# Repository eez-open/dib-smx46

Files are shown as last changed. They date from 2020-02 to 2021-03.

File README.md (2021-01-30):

OSHW-HR000004 (https://certification.oshwa.org/hr000004.html)

The EEZ DIB SMX46 module features programmable 4 x 6 switch matrix,  dual analog outputs and one power relay. 

### Feature list

* On-board STM32F030C6T6 or STM32F031C4T6 MCU
* 2 x 16-pin dual row 3.81 mm connectors
* 2 x ADIB connectors (10-pin 2 mm)
* 4 x 6 switch matrix (24 two-wire crosspoints), max. 2 A 
* 1 x power relay, max. 8 A / 230 Vac
* 2 x analog output 0 - 10 V, 10 mV set resolution (12-bit)
* On-board +3.3 V LDO
* Firmware download via UART
* Optional SWD for debugging
* I2C EEPROM for storing board specific parameters
* Dimensions: 146 x 95 mm, 2-layer PCB

### Firmware repository

https://github.com/eez-open/dib-smx46-fw

### r1B5 prototype

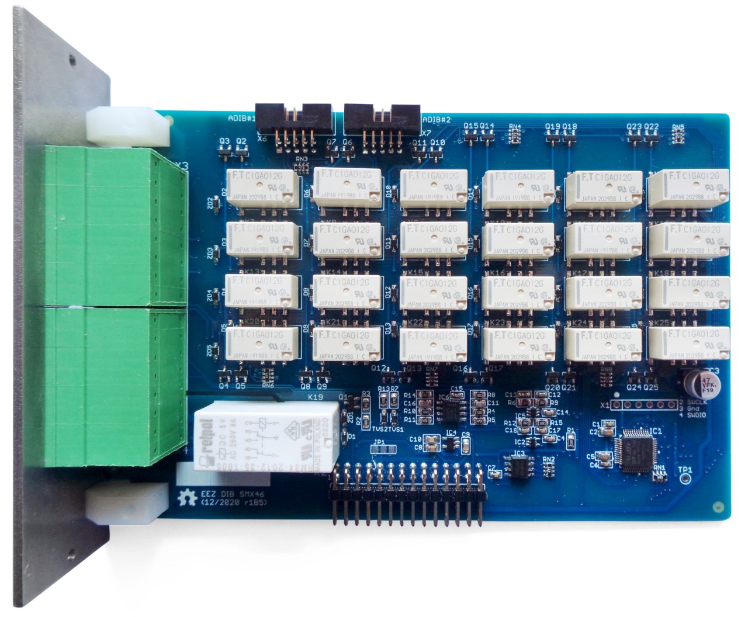
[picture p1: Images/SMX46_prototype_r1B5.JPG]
prototype


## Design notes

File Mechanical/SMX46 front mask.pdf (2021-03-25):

# SMX46

X1

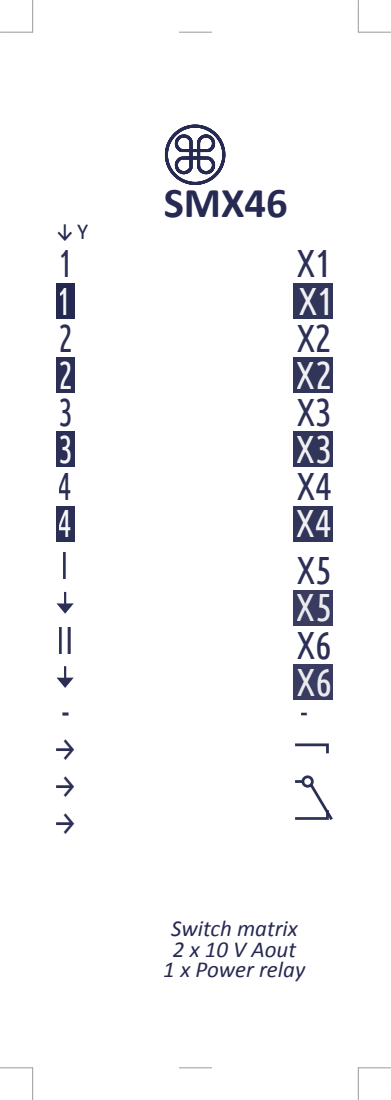
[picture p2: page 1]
Switch matrix 2 x 10 V Aout 1 x Power relay

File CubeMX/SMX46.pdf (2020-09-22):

## SMX46 Project Configuration Report

# 1. Description

## 1.1. Project

Project Name | SMX46
Board Name | custom
Generated with: | STM32CubeMX 5.6.1
Date | 09/22/2020

## 1.2. MCU

MCU Series | STM32F0
MCU Line | STM32F0x0 Value Line
MCU name | STM32F030C6Tx
MCU Package | LQFP48
MCU Pin number | 48

# 2. Pinout Configuration

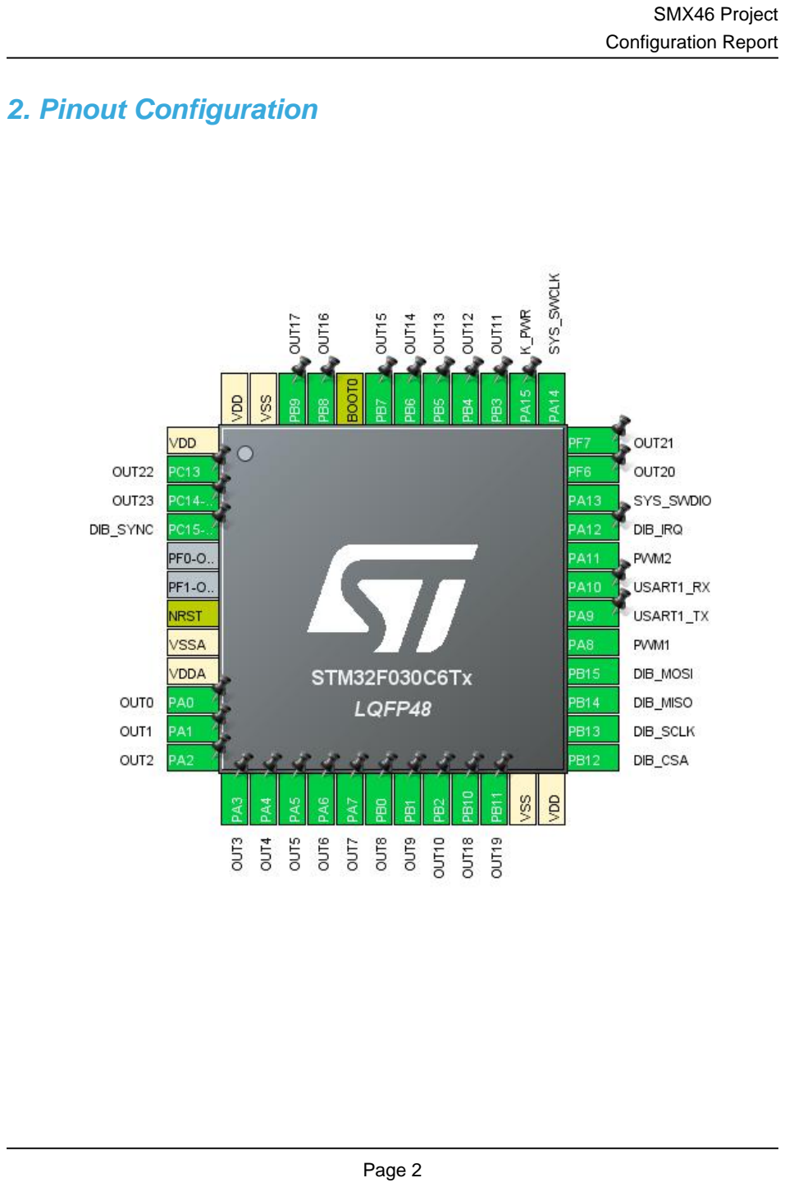
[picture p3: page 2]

# 3. Pins Configuration

Pin Number LQFP48 | Pin Name (function after reset) | Pin Type | Alternate Function(s) | Label
1 | VDD | Power
2 | PC13 * | I/O | GPIO_Output | OUT22
3 | PC14-OSC32_IN * | I/O | GPIO_Output | OUT23
4 | PC15-OSC32_OUT * | I/O | GPIO_Input | DIB_SYNC
7 | NRST | Reset
8 | VSSA | Power
9 | VDDA | Power
10 | PA0 * | I/O | GPIO_Output | OUT0
11 | PA1 * | I/O | GPIO_Output | OUT1
12 | PA2 * | I/O | GPIO_Output | OUT2
13 | PA3 * | I/O | GPIO_Output | OUT3
14 | PA4 * | I/O | GPIO_Output | OUT4
15 | PA5 * | I/O | GPIO_Output | OUT5
16 | PA6 * | I/O | GPIO_Output | OUT6
17 | PA7 * | I/O | GPIO_Output | OUT7
18 | PB0 * | I/O | GPIO_Output | OUT8
19 | PB1 * | I/O | GPIO_Output | OUT9
20 | PB2 * | I/O | GPIO_Output | OUT10
21 | PB10 * | I/O | GPIO_Output | OUT18
22 | PB11 * | I/O | GPIO_Output | OUT19
23 | VSS | Power
24 | VDD | Power
25 | PB12 | I/O | SPI1_NSS | DIB_CSA
26 | PB13 | I/O | SPI1_SCK | DIB_SCLK
27 | PB14 | I/O | SPI1_MISO | DIB_MISO
28 | PB15 | I/O | SPI1_MOSI | DIB_MOSI
29 | PA8 | I/O | TIM1_CH1 | PWM1
30 | PA9 | I/O | USART1_TX
31 | PA10 | I/O | USART1_RX
32 | PA11 | I/O | TIM1_CH4 | PWM2
33 | PA12 * | I/O | GPIO_Output | DIB_IRQ
34 | PA13 | I/O | SYS_SWDIO
35 | PF6 * | I/O | GPIO_Output | OUT20
36 | PF7 * | I/O | GPIO_Output | OUT21
37 | PA14 | I/O | SYS_SWCLK
38 | PA15 * | I/O | GPIO_Output | K_PWR

Pin Number LQFP48 | Pin Name (function after reset) | Pin Type | Alternate Function(s) | Label
39 | PB3 * | I/O | GPIO_Output | OUT11
40 | PB4 * | I/O | GPIO_Output | OUT12
41 | PB5 * | I/O | GPIO_Output | OUT13
42 | PB6 * | I/O | GPIO_Output | OUT14
43 | PB7 * | I/O | GPIO_Output | OUT15
44 | BOOT0 | Boot
45 | PB8 * | I/O | GPIO_Output | OUT16
46 | PB9 * | I/O | GPIO_Output | OUT17
47 | VSS | Power
48 | VDD | Power

## * The pin is affected with an I/O function

# 4. Clock Tree Configuration

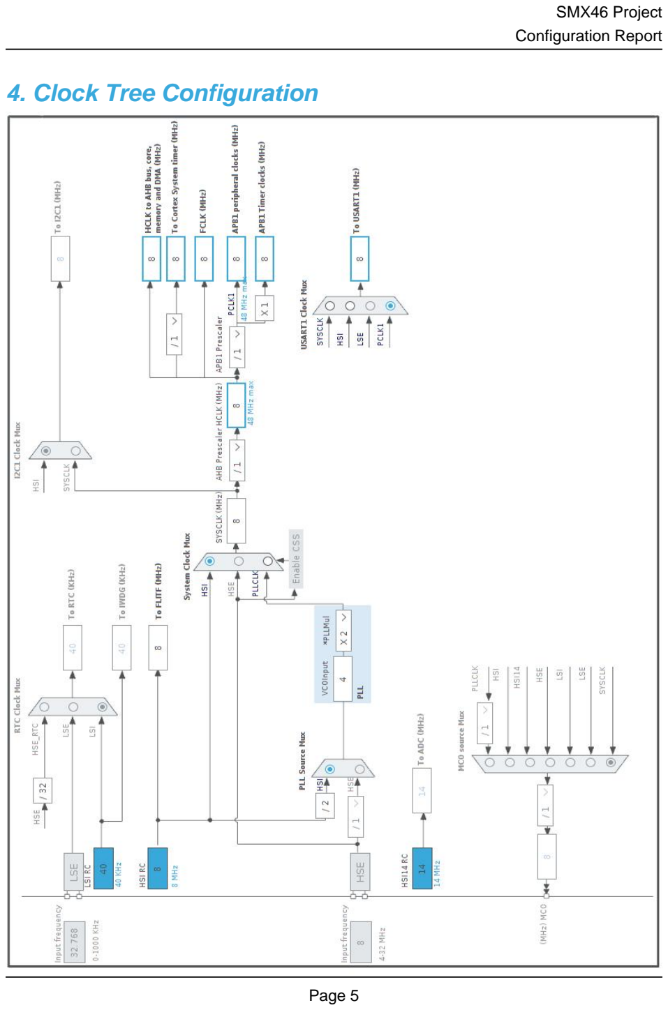
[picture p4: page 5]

# 5. Software Project

## 5.1. Project Settings

Name | Value
Project Name | SMX46
Project Folder | /home/denis/BACKUP/EEZ/Digital control/MCU/STM32/Projects/SMX46
Toolchain / IDE | EWARM V8.32
Firmware Package Name and Version | STM32Cube FW_F0 V1.11.0

## 5.2. Code Generation Settings

Name | Value
STM32Cube MCU packages and embedded software | Copy all used libraries into the project folder
Generate peripheral initialization as a pair of '.c/.h' files | No
Backup previously generated files when re-generating | No
Delete previously generated files when not re-generated | Yes
Set all free pins as analog (to optimize the power consumption) | No

# 6. Power Consumption Calculator report

### 6.1. Microcontroller Selection

Series | STM32F0
Line | STM32F0x0 Value Line
MCU | STM32F030C6Tx
Datasheet | 024849_Rev2

### 6.2. Parameter Selection

Temperature | 25
Vdd | 3.6

### 6.3. Battery Selection

Battery | Li-SOCL2(A3400)
Capacity | 3400.0 mAh
Self Discharge | 0.08 %/month
Nominal Voltage | 3.6 V
Max Cont Current | 100.0 mA
Max Pulse Current | 200.0 mA
Cells in series | 1
Cells in parallel | 1

## 6.4. Sequence

Step | Step1 | Step2
Mode | RUN | STOP
Vdd | 3.6 | 3.6
Voltage Source | Battery | Battery
Range | No Scale | No Scale
Fetch Type | FLASH | n/a
CPU Frequency | 48 MHz | 0 Hz
Clock Configuration | HSE PLL All IPs ON | Regulator_LP
Clock Source Frequency | 8 MHz | 0 Hz

### Peripherals

Additional Cons. | 0 mA | 0 mA
Average Current | 23.46 mA | 7.9 µA
Duration | 0.1 ms | 0.9 ms
DMIPS | 0.0 | 0.0
Ta Max | 100.36 | 105
Category | In DS Table | In DS Table

## 6.5. RESULTS

Sequence Time | 1 ms | Average Current | 2.35 mA
Battery Life | 1 month, 29 days, 16 hours | Average DMIPS | 0.0 DMIPS

## 6.6. Chart

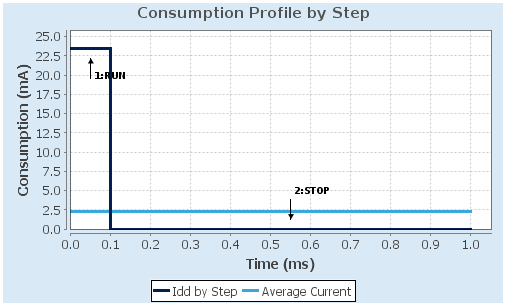
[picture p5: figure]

# 7. IPs and Middleware Configuration

# 7.1. CRC

## mode: Activated 7.1.1. Parameter Settings:

### Basic Parameters:

Default Polynomial State | Enable
Default Init Value State | Enable

### Advanced Parameters:

Input Data Inversion Mode | None
Output Data Inversion Mode | Disable
Input Data Format | Bytes

# 7.2. GPIO

# 7.3. SPI1

## Mode: Full-Duplex Slave Hardware NSS Signal: Hardware NSS Input Signal 7.3.1. Parameter Settings:

### Basic Parameters:

Frame Format | Motorola
Data Size | 4 Bits
First Bit | MSB First

### Clock Parameters:

Clock Polarity (CPOL) | Low
Clock Phase (CPHA) | 1 Edge

### Advanced Parameters:

CRC Calculation | Disabled
NSS Signal Type | Input Hardware

# 7.4. SYS

## mode: Debug Serial Wire Timebase Source: SysTick

# 7.5. TIM1

## Channel1: Output Compare CH1 Channel4: PWM Generation CH4 7.5.1. Parameter Settings:

### Counter Settings:

Prescaler (PSC - 16 bits value) | 0
Counter Mode | Up
Counter Period (AutoReload Register - 16 bits value ) | 0
Internal Clock Division (CKD) | No Division
Repetition Counter (RCR - 8 bits value) | 0
auto-reload preload | Disable

### Trigger Output (TRGO) Parameters:

Master/Slave Mode (MSM bit) | Disable (Trigger input effect not delayed)
Trigger Event Selection | Reset (UG bit from TIMx_EGR)

### Break And Dead Time management - BRK Configuration:

BRK State | Disable
BRK Polarity | High

### Break And Dead Time management - Output Configuration:

Automatic Output State | Disable
Off State Selection for Run Mode (OSSR) | Disable
Off State Selection for Idle Mode (OSSI) | Disable
Lock Configuration | Off

### Output Compare Channel 1:

Mode | Frozen (used for Timing base)
Pulse (16 bits value) | 0
Output compare preload | Disable
CH Polarity | High
CH Idle State | Reset

### PWM Generation Channel 4:

Mode | PWM mode 1
Pulse (16 bits value) | 0
Output compare preload | Enable
Fast Mode | Disable
CH Polarity | High
CH Idle State | Reset

# 7.6. USART1

## Mode: Asynchronous 7.6.1. Parameter Settings:

### Basic Parameters:

Baud Rate | 38400
Word Length | 8 Bits (including Parity)
Parity | None
Stop Bits | 1

### Advanced Parameters:

Data Direction | Receive and Transmit
Over Sampling | 16 Samples
Single Sample | Disable

### Advanced Features:

Auto Baudrate | Disable
TX Pin Active Level Inversion | Disable
RX Pin Active Level Inversion | Disable
Data Inversion | Disable
TX and RX Pins Swapping | Disable
Overrun | Enable
DMA on RX Error | Enable
MSB First | Disable

### * User modified value

# 8. System Configuration

# 8.1. GPIO configuration

IP | Pin | Signal | GPIO mode | GPIO pull/up pull down

## Max Speed

## User Label

SPI1 | PB12 | SPI1_NSS | Alternate Function Push Pull | No pull-up and no pull-down | High * | DIB_CSA
| PB13 | SPI1_SCK | Alternate Function Push Pull | No pull-up and no pull-down | High * | DIB_SCLK
| PB14 | SPI1_MISO | Alternate Function Push Pull | No pull-up and no pull-down | High * | DIB_MISO
| PB15 | SPI1_MOSI | Alternate Function Push Pull | No pull-up and no pull-down | High * | DIB_MOSI
SYS | PA13 | SYS_SWDIO | n/a | n/a | n/a
| PA14 | SYS_SWCLK | n/a | n/a | n/a
TIM1 | PA8 | TIM1_CH1 | Alternate Function Push Pull | No pull-up and no pull-down | Low | PWM1
| PA11 | TIM1_CH4 | Alternate Function Push Pull | No pull-up and no pull-down | Low | PWM2
USART1 | PA9 | USART1_TX | Alternate Function Push Pull | No pull-up and no pull-down | High *
| PA10 | USART1_RX | Alternate Function Push Pull | No pull-up and no pull-down | High *
GPIO | PC13 | GPIO_Output | Output Push Pull | No pull-up and no pull-down | Low | OUT22
| PC14- OSC32_IN | GPIO_Output | Output Push Pull | No pull-up and no pull-down | Low | OUT23
| PC15- OSC32_OU T | GPIO_Input | Input mode | No pull-up and no pull-down | n/a | DIB_SYNC
PA0 | GPIO_Output | Output Push Pull | No pull-up and no pull-down | Low | OUT0
PA1 | GPIO_Output | Output Push Pull | No pull-up and no pull-down | Low | OUT1
PA2 | GPIO_Output | Output Push Pull | No pull-up and no pull-down | Low | OUT2
PA3 | GPIO_Output | Output Push Pull | No pull-up and no pull-down | Low | OUT3
PA4 | GPIO_Output | Output Push Pull | No pull-up and no pull-down | Low | OUT4
PA5 | GPIO_Output | Output Push Pull | No pull-up and no pull-down | Low | OUT5
PA6 | GPIO_Output | Output Push Pull | No pull-up and no pull-down | Low | OUT6
PA7 | GPIO_Output | Output Push Pull | No pull-up and no pull-down | Low | OUT7
PB0 | GPIO_Output | Output Push Pull | No pull-up and no pull-down | Low | OUT8
PB1 | GPIO_Output | Output Push Pull | No pull-up and no pull-down | Low | OUT9
PB2 | GPIO_Output | Output Push Pull | No pull-up and no pull-down | Low | OUT10
PB10 | GPIO_Output | Output Push Pull | No pull-up and no pull-down | Low | OUT18
PB11 | GPIO_Output | Output Push Pull | No pull-up and no pull-down | Low | OUT19
PA12 | GPIO_Output | Output Push Pull | No pull-up and no pull-down | Low | DIB_IRQ
PF6 | GPIO_Output | Output Push Pull | No pull-up and no pull-down | Low | OUT20
PF7 | GPIO_Output | Output Push Pull | No pull-up and no pull-down | Low | OUT21
PA15 | GPIO_Output | Output Push Pull | No pull-up and no pull-down | Low | K_PWR
PB3 | GPIO_Output | Output Push Pull | No pull-up and no pull-down | Low | OUT11
PB4 | GPIO_Output | Output Push Pull | No pull-up and no pull-down | Low | OUT12

IP | Pin | Signal | GPIO mode | GPIO pull/up pull down | Max Speed | User Label
| PB5 | GPIO_Output | Output Push Pull | No pull-up and no pull-down | Low | OUT13
| PB6 | GPIO_Output | Output Push Pull | No pull-up and no pull-down | Low | OUT14
| PB7 | GPIO_Output | Output Push Pull | No pull-up and no pull-down | Low | OUT15
| PB8 | GPIO_Output | Output Push Pull | No pull-up and no pull-down | Low | OUT16
| PB9 | GPIO_Output | Output Push Pull | No pull-up and no pull-down | Low | OUT17

# 8.2. DMA configuration

DMA request | Stream | Direction | Priority
SPI1_RX | DMA1_Channel2 | Peripheral To Memory | Low
SPI1_TX | DMA1_Channel3 | Memory To Peripheral | Low

## SPI1_RX: DMA1_Channel2 DMA request Settings:

Mode: | Normal
Peripheral Increment: | Disable
Memory Increment: | Enable *
Peripheral Data Width: | Byte
Memory Data Width: | Byte

## SPI1_TX: DMA1_Channel3 DMA request Settings:

Mode: | Normal
Peripheral Increment: | Disable
Memory Increment: | Enable *
Peripheral Data Width: | Byte
Memory Data Width: | Byte

# 8.3. NVIC configuration

Interrupt Table | Enable | Preenmption Priority | SubPriority
Non maskable interrupt | true | 0 | 0
Hard fault interrupt | true | 0 | 0
System service call via SWI instruction | true | 0 | 0
Pendable request for system service | true | 0 | 0
System tick timer | true | 0 | 0
DMA1 channel 2 and 3 interrupts | true | 0 | 0
Flash global interrupt | unused
RCC global interrupt | unused
TIM1 break, update, trigger and commutation interrupts | unused
TIM1 capture compare interrupt | unused
SPI1 global interrupt | unused
USART1 global interrupt | unused

### * User modified value

# 9. Predefined Views - Category view : Current

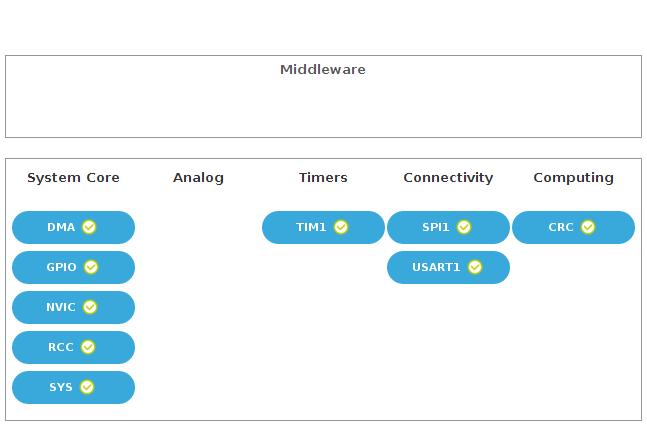
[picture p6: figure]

# 10. Software Pack Report

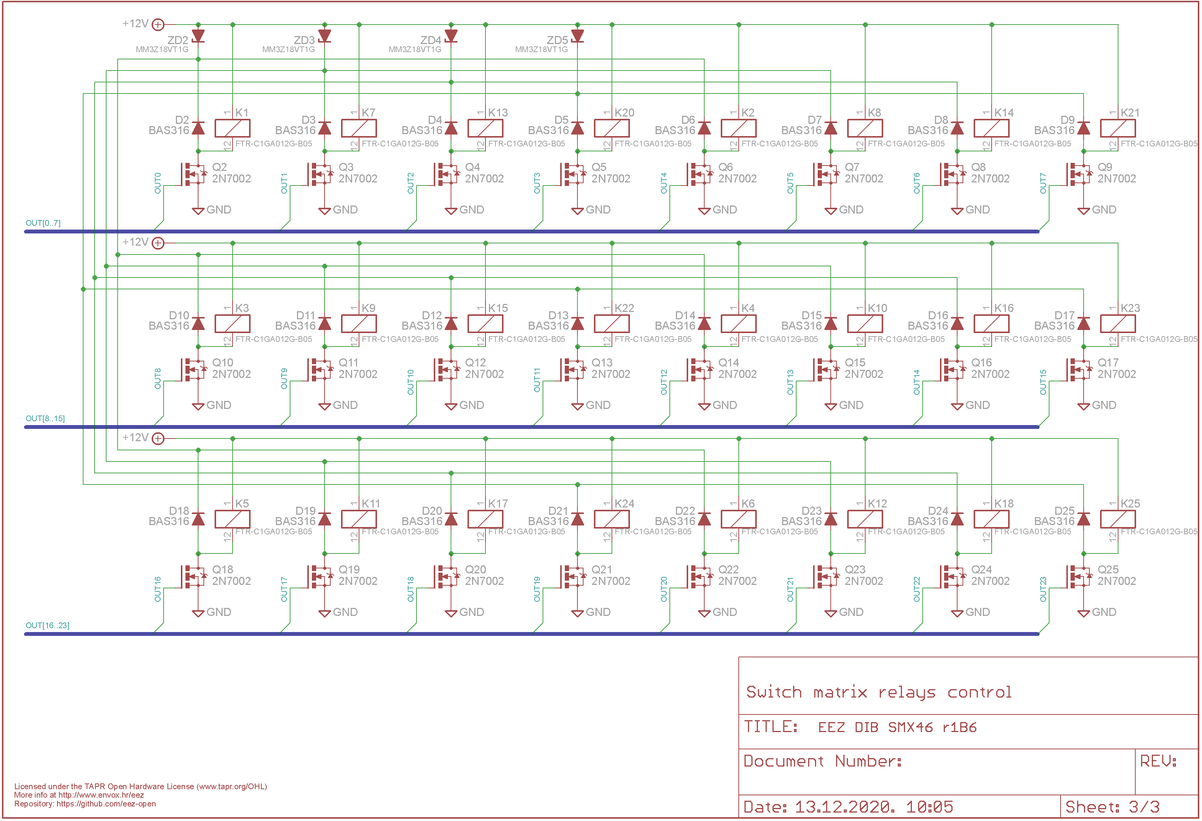
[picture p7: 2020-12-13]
EEZ DIB SMX46 r1B6 Sheet3of3.png

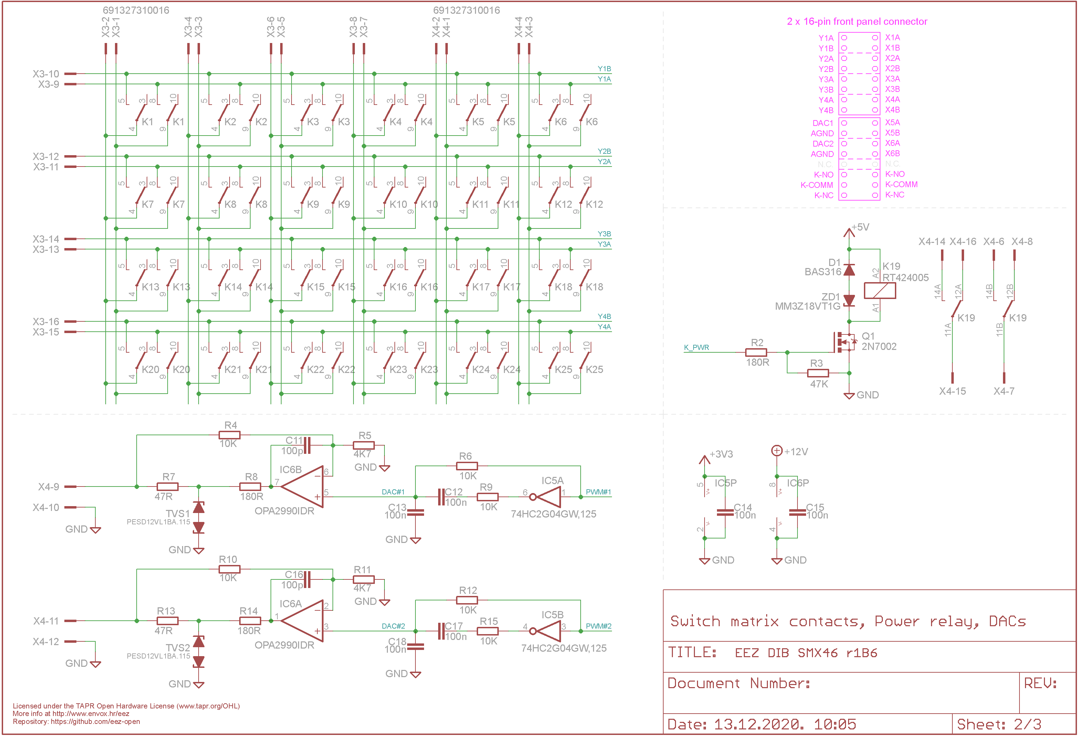
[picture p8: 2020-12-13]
EEZ DIB SMX46 r1B6 Sheet2of3.png

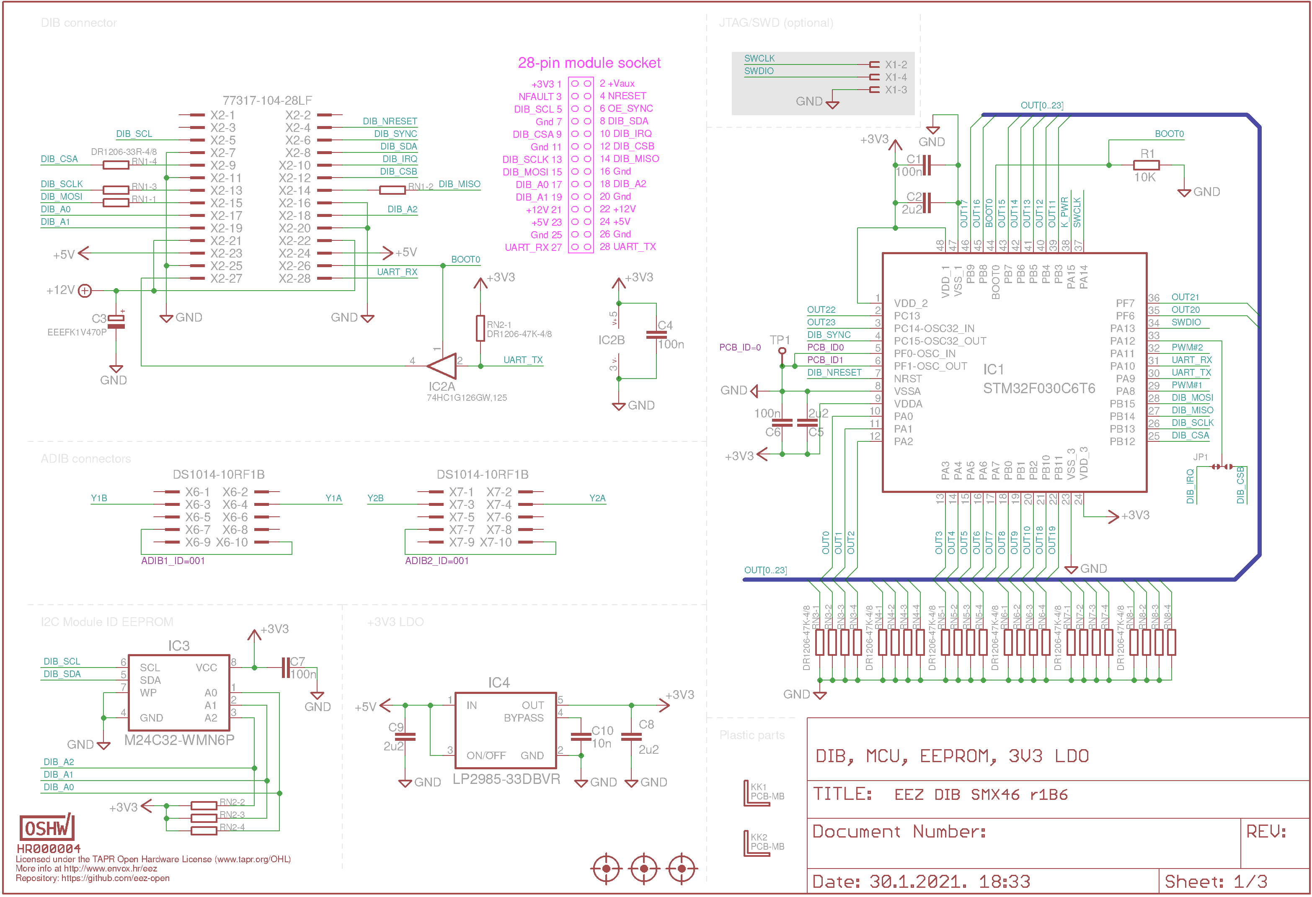
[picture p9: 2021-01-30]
EEZ DIB SMX46 r1B6 Sheet1of3.png

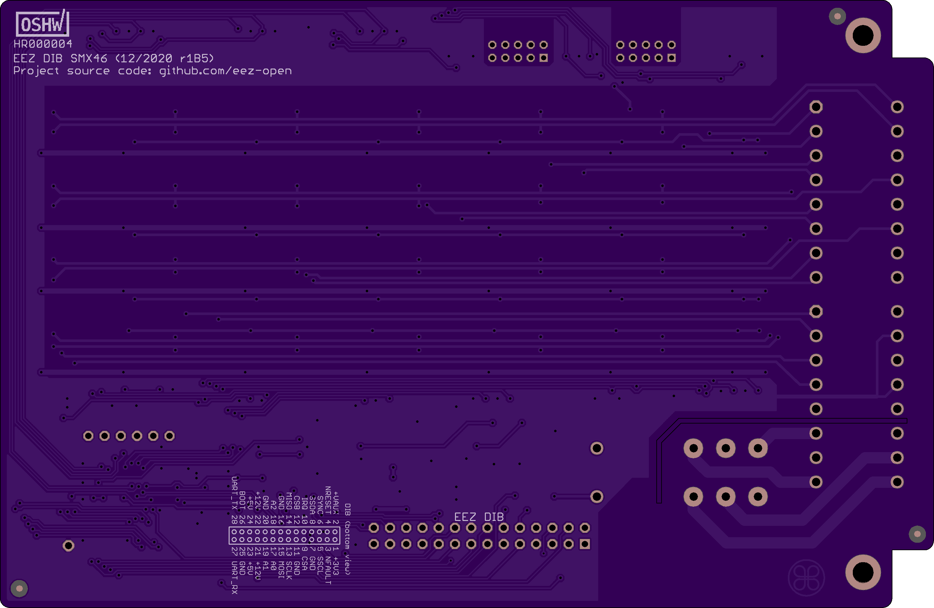
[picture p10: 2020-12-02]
Images/EEZ_DIB_SMX46_PCB_bottom.png

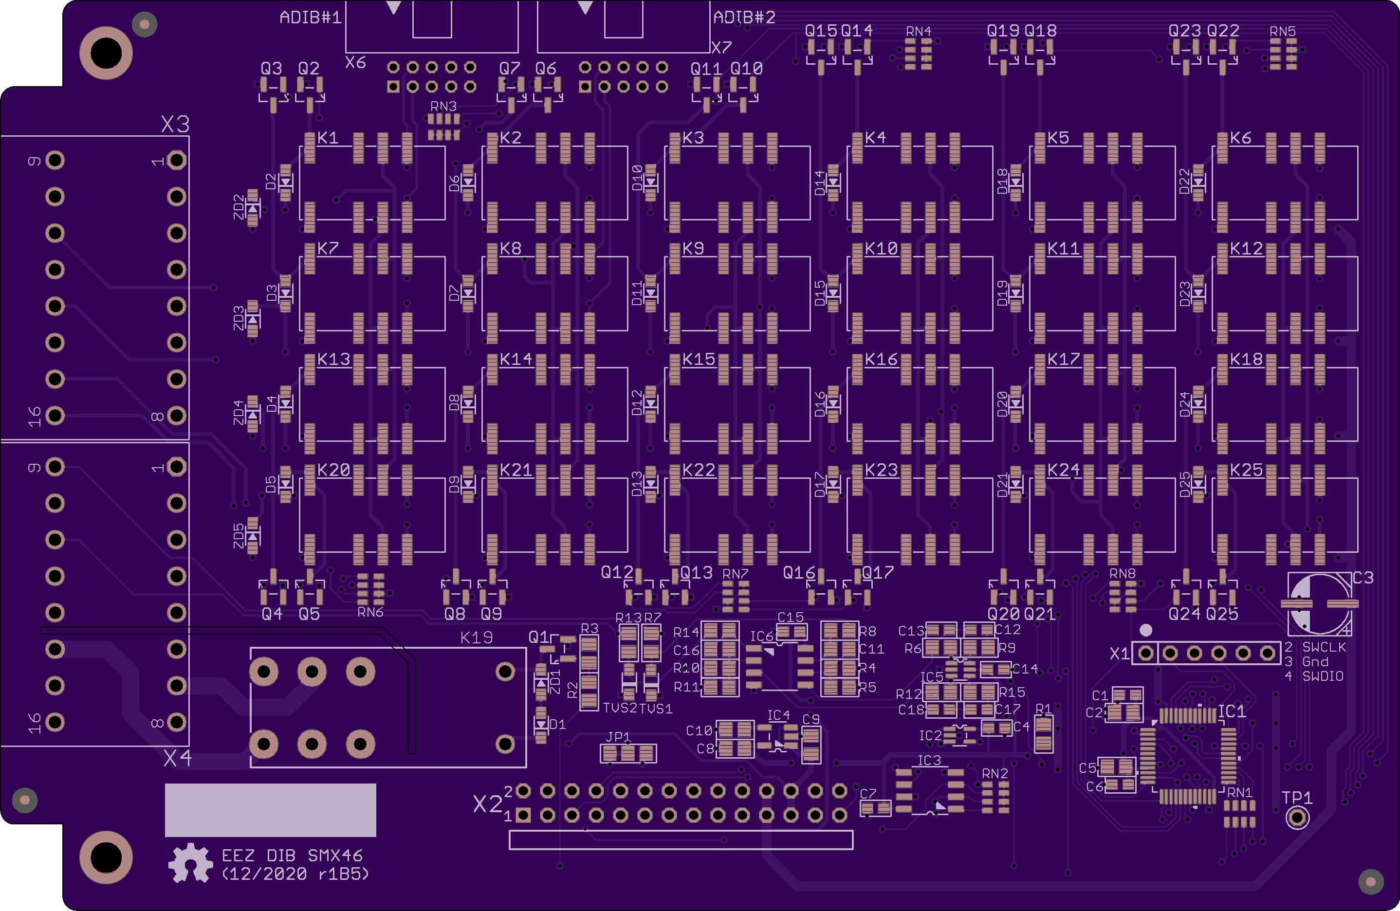
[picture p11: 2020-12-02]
Images/EEZ_DIB_SMX46_PCB_top.png

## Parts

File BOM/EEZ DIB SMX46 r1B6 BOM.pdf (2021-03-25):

EEZ DIB SMX46 BOM (r1B6, 2021-03-25) Project source code at https://github.com/eez-open/dib-prel6
Farnell / Element14 # Unit price Qty Part name Package Reference designator Code Part Number MOQ € | Digi-Key Unit price Part Number MOQ € | Mouser Unit price Part Number MOQ €
| | 80-C0603C104M4R
VJ0805Y103JXXP W1BC | | 710-885012207122
| | 80-C0805C101K5G
GRM21BR71C225 KA12L | | 80-C0805C225M4R ECLR
| | 667-EEE-FK1V470P

D1, D2, D3, D4, D5, D6, D7, D8, D9, D10, D11, D12, D13, D14, D15, D16, D17, D18, D19, D20, D21, D22, D23, D24, D25

| STM32F030C6T 6TR | 511-STM32F030C6T
Option: 2849912 STM32F031C4T6 2,510 1 STM32F031C4T6 | 497-13617-ND 2,200 | 6 STM32F031C4T 2,110 1 6
| | 771-HC1G126GW125
| | 511-M24C32-WMN6P
| | 595-LP2985-33DBVR
74HC2G04GW,125 74HC2G04GW,125 | | 771-HC2G04GW125
| | OPA2990IDR
K1, K2, K3, K4, K5, K6, K7, K8, K9, K10, K11, K12, K13, K14, K15, K16, K17, K18, K20, K21, K22, K23, K24, K2 | | 817-FTR-C1GA012GB05
1 | 10 100n | 0603 | 2522597 | 0,011 10 | 490-4774-1-ND | 0,029 100 | 0,007 100
2 | 1 10n | 0805 | C10 | 2896555 | 0,065 10 | 490-7194-1-ND | 0,017 | 10 | 0,036 10
3 | 2 100p | C0G, 0805 | C11, C16 | 2896861 | 0,023 10 | 399-15000-1-ND | 0,019 | 10 | 0,032 10
4 | 3 2u2 | 0805 | C2, C6, C8, C9 | 1828829 | 0,198 | 5 | 1276-2954-1-ND | 0,085 | 10 | 0,078 10
5 | 1 EEEFK1V470P | C3 | 9695850 | EEEFK1V470P | 0,344 | 1 | PCE3842CT-ND | 0,312 | 10 | 0,238 10
6 | 25 BAS316 | SOD-323 | 8734275 | BAS316,115 | 0,193 | 5 | 1727-7370-1-ND | 0,120 | 1 | 771-BAS316-T/R | 0,179 | 1
7 | 1 STM32F030C6T6 | LQFP-48 | IC1 | 2393632 | STM32F030C6T6 | 1,350 | 1 | 1,360 | 1 | 1,360 | 1
8 | 1 74HC1G126GW.125 | TSSOP-5 | IC2 | - | | | 1727-6037-1-ND | 0,360 | 1 | 0,369 | 1
9 | 1 M24C32-WMN6P | SOIC-8 | IC3 | 1224413 | M24C32-WMN6P | 0,212 | 5 | - | 0,210 | 1
10 | 1 | SOT-23-5 | IC4 | 1053660 | 0,610 | 1 | 296-18476-1-ND | 0,540 | 1 | 0,507 | 1
11 | 1 | IC5 | 2777732 | 0,283 | 5 | 1727-6045-1-ND | 0,274 | 10 | 0,248 10
12 | 1 | SOIC-8 | IC6 | - | | | 296-53506-1-ND | 1,210 | 1 | 1,360 | 1
13 | 24 FTR-C1GA012G-B05 | - | - | 3,320 10
14 | 1 RT424005 | K19 | 1629052 | RT424005 | 2,640 | 1 | PB1998-ND | 3,620 | 1 | 655-RT424005 | 2,820 | 1
15 | 25 2N7002 | SOT-23 | 1713825 | 2N7002K-7 | 0,148 | 5 | 0,126 | 10 | 0,113 10
16 | 7 10K | 0805 | 9237755 | 0,022 10 | 0,039 | 10 | 0,014 10
17 | 2 180R | 0805 | R2, R8, R14 | 2447583 | 0,007 10 | A126343CT-ND | 0,038 | 10 | 0,030 10
18 | 1 47K | 0805 | R3 | 2447664 | 0,009 10 | RHM47KKCT-ND | 0,036 | 10 | 0,014 10
19 | 2 4K7 | 0805 | R5, R11 | 2861530 | CRGCQ0805F4K7 | 0,012 10 | 0,040 | 10 | 0,027 10

C1, C4, C5, C7, C12, C13,
C14, C15, C17, C18

C0603C104K4RAC
7081

C0805C101JAGAC
TU
LP2985-33DBVR | LP2985A- 33DBVTE4 .
OPA2990IDR | 595-

THT; 8A relay
Q1, Q2, Q3, Q4, Q5, Q6, Q7, Q8, Q9, Q10, Q11, Q12, Q13, Q14, Q15, Q16, Q17, Q18, Q19, Q20, Q21, Q22, Q23, Q24, Q25 | T2N7002AKLMC T-ND | 757-T2N7002AKLM
| ND | 603-RC0805FR-0710KL
MCWR08X1800FT L | | 652-CR0805FX-1800ELF
| | 603-RC0805FR-0747KL
| 311-4.70KCRCT-ND | 603-RC0805FR-074K7L

R1, R4, R6, R9, R10, R12,
R15
RC0805FR-0710KL | 311-10.0KCRCT-

MCWR08X4702FT
L

# Qty Part name | RS Components | TME | Price calculation for 1 set

Unit price Code Part Number MOQ € | Unit price Code / Part Number MOQ € | THT SMD | | Line Cost €

1 10 100n

2 1 10n

3 2 100p

4 3 2u2

5 1 EEEFK1V470P

6 25 BAS316

7 1 STM32F030C6T6

8 1 74HC1G126GW.125

9 1 M24C32-WMN6P

10 1

11 1

12 1

13 24 FTR-C1GA012G-B05

14 1 RT424005
15 25 2N7002

16 7 10K

17 2 180R

18 1 47K

19 2 4K7

Option:
STM32F031C4T6

LP2985-33DBVR

74HC2G04GW,125

OPA2990IDR

393-6952 | 0,069 25 | CL10B104KA8NNNC | 0,098 100 | 10 | Mouser | 0,007 € 10 | 0,070
464-6672 | 0,026 50 | CC0805KRX7R9103 | 0,027 100 | 1 | Digikey | 0,017 € | 1 | 0,017
461-3997 | 0,030 50 | CL21C101JBANNNC | 0,026 100 | 2 | Digikey | 0,019 € | 2 | 0,038
766-1031 | 0,069 100 | CL21B225KOFNNNG | 0,071 100 | 3 | RS | 0,069 € | 3 | 0,207
537-0657 EEEFK1V470P | 0,394 | 5 | EEEFK1V470P | 0,130 | 5 | 1 | TME | 0,130 € | 1 | 0,130
397-2914 BAS316,115 | 0,122 50 | BAS316,115 | 0,026 25 | 25 | TME | 0,026 € 25 | 0,661
192-0993 | 0,972 | 5 | STM32F030C6T6 | 0,940 | 4 | 1 | TME | 0,940 € | 1 | 0,940
192-1080 | 2,152 | 5 | STM32F031C4T6 | 2,050 | 1
813-9282 | 0,024 100 | 74HC1G126GW.125 | 0,062 10 | 1 | RS | 0,024 € | 1 | 0,024
686-2453 | 0,180 25 | M24C32-WMN6P | 0,165 | 3 | 1 | TME | 0,165 € | 1 | 0,165
660-6733 LP2985-33DBVT | 0,737 | 1 | LP2985-33DBVR | 0,362 | 1 | 1 | TME | 0,362 € | 1 | 0,362
153-2919 | 0,235 50 | 74HC2G04GW.125 | 0,138 | 5 | 1 | TME | 0,138 € | 1 | 0,138
- | | | - | | | 1 | Digikey | 1,210 € | 1 | 1,210
195-8097 FTR-C1GA012G | 3,200 20 | FTR-C1GA012G-B05 | 0,840 25 | 24 | TME | 0,840 € 24 | 20,160
- | RT424005 | 1,150 | 5 | 1 | TME | 1,150 € | 1 | 1,150
671-0312 2N7002 | 1,250 20 | 2N7002LT1G | 0,019 25 | 25 | TME | 0,019 € 25 | 0,480
125-1189 CRG0805F10K | 0,002 100 | RC0805FR-0710K | 0,022 100 | 7 | RS | 0,002 € | 7 | 0,014
223-0326 CRG0805F180R | 0,090 50 | CQ05S8F1800T5E | 0,026 100 | 2 | Farnell | 0,007 € | 2 | 0,014
679-1434 | 0,036 50 | RC0805FR-0747K | 0,022 100 | 1 | Farnell | 0,009 € | 1 | 0,009
223-0528 CRG0805F4K7 | 0,023 50 | 0805S8F4701T5E | 0,023 100 | 2 | Farnell | 0,012 € | 2 | 0,023

Best
Supplier

Lowest
unit price
€

Order
Qty

VJ0603Y104KXJ
AT
08055C103KAT
2A
CC0805JRNP09
BN101
CL21B225KAFN
NNF

STM32F030C6T
6TR
STM32F031C4T
6
74HC1G126GW,
125
M24C32-
WMN6P

74HC2G04GW,1
25

CRCW080547K
0FKEA

Farnell / Element14 # Qty Part name Package Reference designator Code Part Number MOQ € | Digi-Key Part Number Unit price MOQ € | Mouser Part Number Unit price MOQ Unit price €
| | 279-CRGCQ0805F47 R
| CAY16-330J4LFCT-ND | 652-CAY16-330J4LF
| | 652-CAY16-473J4LF
PESD12VL1BA,11 5 | | 771-PESD12VL1BA-T/R
| | 649-77317-104-28LF
THT, 16-pin 3.81mm terminal MCD 1,5/ 8-G1-block header, male pins 3,81 | 732-691327310016-ND
20 | 2 47R | 0805 | R7, R13 | 2861899 | CRGCQ0805J47R | 0,007 10 | P47.0CCT-ND | 0,069 | 10 | 0,028 10
21 | 1 DR1206-33R-4/8 | 1206 resistor array | RN1 | 1770128 | CAY16-330J4LF | 0,069 10 | 0,090 | 1 | 0,085 | 1
22 | 7 | 1206 resistor array | 2787793 | CAY16-4702F4LF | 0,178 10 | CAY16-473J4LF | 0,080 | 10 | 0,016 10
23 | 2 PESD12VL1BA,115 | SOD-323 | TVS1, TVS2 | 8737363 | 0,365 | 5 | 1727-3808-1-ND | 0,320 | 10 | 0,296 10
24 | 1 77317-104-28LF | X2 | - | S2111EC-14-ND | 1,030 | 1 | 1,540 | 1
25 | 2 691327310016 | X3, X4 | 1793077 | 5,770 | 1 | 7,810 | 1 | 651-1843130 | 9,270 | 1
26 | 2 DS1014-10RF1B | X6, X7 | - | 2BHR-10-HUA | 0,650 | 1 | -
27 | 5 MM3Z18VT1G | SOD-323 | ZD1, ZD2, ZD3, ZD4, ZD5 | 1431193 | MM3Z18VT1G | 0,109 10 | 0,103 | 10 | 0,108 10

Not installed
1 N.C. | X1

Related parts and accessories
2 PMB-1 | PCB bracket; polyamide | KK1, KK2 | - | - | -
4 TJ0831530000G | 2579776 | EBK-08-B | 2,400 | 1 | 609-3803-ND | 1,760 | 1 | 1,530 | 1

Custom made components
1 | -
| All prices are net prices (without VAT)

All resistors are 1% 0805 and all capacitors are X7R 0805 if not otherwise specified.

DR1206-47K-4/8 | RN2, RN3, RN4, RN5, RN6, RN7, RN8

THT, 28-pin 0.1" header right angled

THT, 10-pin 2mm IDC, right angle
MM3Z18VT1GO
SCT-ND

863-
MM3Z18VT1G

8-pin 3.81mm pluggable
terminal block

649-220004-
D081B01LF

PCB 2-layer 146 x 95
mm

Please note that BOM does not contain ordering number for parts on reels or that which includes re-reeling fee (e.g. Farnell). Take also into account that total cost is higher because min. quantity (MOQ) for many parts is larger then what is needed for single unit.

# Qty Part name | RS Components | TME | Price calculation for 1 set

Code Part Number MOQ € | Code / Part Number Unit price MOQ € | THT SMD | | Line Cost € Unit price

20 2 47R

21 1 DR1206-33R-4/8

22 7

23 2 PESD12VL1BA,115

24 1 77317-104-28LF

25 2 691327310016

26 2 DS1014-10RF1B

27 5 MM3Z18VT1G

Not installed
1 N.C.

Related parts and accessories 2 PMB-1
4 TJ0831530000G

Custom made components
1

DR1206-47K-4/8

PCB 2-layer 146 x 95
mm

Best
Supplier

Lowest
unit price
€

Order
Qty
223-0253 CRG0805F47R | 0,016 50 | SMD0805-47R-1% | 0,022 100 | 2 | Farnell | 0,007 € | 2 | 0,013
522-5670 CAY16-330J4LF | 0,004 50 | 4D03WGJ0330T | 0,009 100 | 1 | RS | 0,004 € | 1 | 0,004
522-5759 CAY16-473J4LF | 0,020 50 | 4D03WGJ0473T | 0,013 100 | 7 | TME | 0,013 € | 7 | 0,091
508-024 | 0,294 20 | PESD12VL1BA.115 | 0,126 | 5 | 2 | TME | 0,126 € | 2 | 0,252
- | - | 1 | Digikey | 1,030 € | 1 | 1,030
191-1724 691327310016 | 7,900 | 1 | - | 2 | Farnell | 5,770 € | 2 | 11,540
- | DS1014-10RF1B | 0,220 | 3 | 2 | TME | 0,220 € | 2 | 0,440
802-4574 MM3Z18VT1G | 0,038 200 | MM3Z18VT1G | 0,025 25 | 5 | TME | 0,025 € | 5 | 0,126
6 | 126 | 39,31 €
1 | Farnell | 0,000 € | 1 | 0,000
- | PMB-1 | 0,072 10 | TME | 0,072 € | 2 | 0,145
- | 1,430 | 1 | TME | 1,430 € | 4 | 5,720

5,86 €

JLCPCB | 6,244 € | 1 | 6,244
| | | 6,24 €
| | Total | 51,42 €

PESD12VL1BA,
115

15EDGK-3.81-08P-14-
00A(H)

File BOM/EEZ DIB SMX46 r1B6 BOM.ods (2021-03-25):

 |  |  |  |  | Farnell / Element14 |  |  |  | Digi-Key |  |  | Mouser |  |  | RS Components |  |  |  | TME |  |  |  |  | Price calculation for 1 set
# | Qty | Part name | Package | Reference designator | Code | Part Number | Unit price € | MOQ | Part Number | Unit price € | MOQ | Part Number | Unit price € | MOQ | Code | Part Number | Unit price € | MOQ | Code / Part Number | Unit price € | MOQ | THT | SMD | Best Supplier | Lowest unit price € | Order Qty | Line Cost €
1 | 10 | 100n | 0603 | C1, C4, C5, C7, C12, C13, C14, C15, C17, C18 | 2522597 | C0603C104K4RAC7081 | 0,011 | 10 | 490-4774-1-ND | 0,029 | 100 | 80-C0603C104M4R | 0,007 | 100 | 393-6952 | VJ0603Y104KXJAT | 0,069 | 25 | CL10B104KA8NNNC | 0,098 | 100 |  | 10 | Mouser | 0,007 € | 10 | 0,070
2 | 1 | 10n | 0805 | C10 | 2896555 | VJ0805Y103JXXPW1BC | 0,065 | 10 | 490-7194-1-ND | 0,017 | 10 | 710-885012207122 | 0,036 | 10 | 464-6672 | 08055C103KAT2A | 0,026 | 50 | CC0805KRX7R9103 | 0,027 | 100 |  | 1 | Digikey | 0,017 € | 1 | 0,017
3 | 2 | 100p | C0G, 0805 | C11, C16 | 2896861 | C0805C101JAGACTU | 0,023 | 10 | 399-15000-1-ND | 0,019 | 10 | 80-C0805C101K5G | 0,032 | 10 | 461-3997 | CC0805JRNP09BN101 | 0,030 | 50 | CL21C101JBANNNC | 0,026 | 100 |  | 2 | Digikey | 0,019 € | 2 | 0,038
4 | 3 | 2u2 | 0805 | C2, C6, C8, C9 | 1828829 | GRM21BR71C225KA12L | 0,198 | 5 | 1276-2954-1-ND | 0,085 | 10 | 80-C0805C225M4RECLR | 0,078 | 10 | 766-1031 | CL21B225KAFNNNF | 0,069 | 100 | CL21B225KOFNNNG | 0,071 | 100 |  | 3 | RS | 0,069 € | 3 | 0,207
5 | 1 | EEEFK1V470P |  | C3 | 9695850 | EEEFK1V470P | 0,344 | 1 | PCE3842CT-ND | 0,312 | 10 | 667-EEE-FK1V470P | 0,238 | 10 | 537-0657 | EEEFK1V470P | 0,394 | 5 | EEEFK1V470P | 0,130 | 5 |  | 1 | TME | 0,130 € | 1 | 0,130
6 | 25 | BAS316 | SOD-323 | D1, D2, D3, D4, D5, D6, D7, D8, D9, D10, D11, D12, D13, D14, D15, D16, D17, D18, D19, D20, D21, D22, D23, D24, D25 | 8734275 | BAS316,115 | 0,193 | 5 | 1727-7370-1-ND | 0,120 | 1 | 771-BAS316-T/R | 0,179 | 1 | 397-2914 | BAS316,115 | 0,122 | 50 | BAS316,115 | 0,026 | 25 |  | 25 | TME | 0,026 € | 25 | 0,661
7 | 1 | STM32F030C6T6 | LQFP-48 | IC1 | 2393632 | STM32F030C6T6 | 1,350 | 1 | STM32F030C6T6TR | 1,360 | 1 | 511-STM32F030C6T6 | 1,360 | 1 | 192-0993 | STM32F030C6T6TR | 0,972 | 5 | STM32F030C6T6 | 0,940 | 4 |  | 1 | TME | 0,940 € | 1 | 0,940
 |  | Option: STM32F031C4T6 |  |  | 2849912 | STM32F031C4T6 | 2,510 | 1 | 497-13617-ND | 2,200 |  | STM32F031C4T6 | 2,110 | 1 | 192-1080 | STM32F031C4T6 | 2,152 | 5 | STM32F031C4T6 | 2,050 | 1
8 | 1 | 74HC1G126GW.125 | TSSOP-5 | IC2 | - |  |  |  | 1727-6037-1-ND | 0,360 | 1 | 771-HC1G126GW125 | 0,369 | 1 | 813-9282 | 74HC1G126GW,125 | 0,024 | 100 | 74HC1G126GW.125 | 0,062 | 10 |  | 1 | RS | 0,024 € | 1 | 0,024
9 | 1 | M24C32-WMN6P | SOIC-8 | IC3 | 1224413 | M24C32-WMN6P | 0,212 | 5 | - |  |  | 511-M24C32-WMN6P | 0,210 | 1 | 686-2453 | M24C32-WMN6P | 0,180 | 25 | M24C32-WMN6P | 0,165 | 3 |  | 1 | TME | 0,165 € | 1 | 0,165
10 | 1 | LP2985-33DBVR | SOT-23-5 | IC4 | 1053660 | LP2985A-33DBVTE4 . | 0,610 | 1 | 296-18476-1-ND | 0,540 | 1 | 595-LP2985-33DBVR | 0,507 | 1 | 660-6733 | LP2985-33DBVT | 0,737 | 1 | LP2985-33DBVR | 0,362 | 1 |  | 1 | TME | 0,362 € | 1 | 0,362
11 | 1 | 74HC2G04GW,125 |  | IC5 | 2777732 | 74HC2G04GW,125 | 0,283 | 5 | 1727-6045-1-ND | 0,274 | 10 | 771-HC2G04GW125 | 0,248 | 10 | 153-2919 | 74HC2G04GW,125 | 0,235 | 50 | 74HC2G04GW.125 | 0,138 | 5 |  | 1 | TME | 0,138 € | 1 | 0,138
12 | 1 | OPA2990IDR | SOIC-8 | IC6 | - |  |  |  | 296-53506-1-ND | 1,210 | 1 | 595-OPA2990IDR | 1,360 | 1 | - |  |  |  | - |  |  |  | 1 | Digikey | 1,210 € | 1 | 1,210
13 | 24 | FTR-C1GA012G-B05 |  | K1, K2, K3, K4, K5, K6, K7, K8, K9, K10, K11, K12, K13, K14, K15, K16, K17, K18, K20, K21, K22, K23, K24, K2 | - |  |  |  | - |  |  | 817-FTR-C1GA012GB05 | 3,320 | 10 | 195-8097 | FTR-C1GA012G | 3,200 | 20 | FTR-C1GA012G-B05 | 0,840 | 25 |  | 24 | TME | 0,840 € | 24 | 20,160
14 | 1 | RT424005 | THT; 8A relay | K19 | 1629052 | RT424005 | 2,640 | 1 | PB1998-ND | 3,620 | 1 | 655-RT424005 | 2,820 | 1 | - |  |  |  | RT424005 | 1,150 | 5 | 1 |  | TME | 1,150 € | 1 | 1,150
15 | 25 | 2N7002 | SOT-23 | Q1, Q2, Q3, Q4, Q5, Q6, Q7, Q8, Q9, Q10, Q11, Q12, Q13, Q14, Q15, Q16, Q17, Q18, Q19, Q20, Q21, Q22, Q23, Q24, Q25 | 1713825 | 2N7002K-7 | 0,148 | 5 | T2N7002AKLMCT-ND | 0,126 | 10 | 757-T2N7002AKLM | 0,113 | 10 | 671-0312 | 2N7002 | 1,250 | 20 | 2N7002LT1G | 0,019 | 25 |  | 25 | TME | 0,019 € | 25 | 0,480
16 | 7 | 10K | 0805 | R1, R4, R6, R9, R10, R12, R15 | 9237755 | RC0805FR-0710KL | 0,022 | 10 | 311-10.0KCRCT-ND | 0,039 | 10 | 603-RC0805FR-0710KL | 0,014 | 10 | 125-1189 | CRG0805F10K | 0,002 | 100 | RC0805FR-0710K | 0,022 | 100 |  | 7 | RS | 0,002 € | 7 | 0,014
17 | 2 | 180R | 0805 | R2, R8, R14 | 2447583 | MCWR08X1800FTL | 0,007 | 10 | A126343CT-ND | 0,038 | 10 | 652-CR0805FX-1800ELF | 0,030 | 10 | 223-0326 | CRG0805F180R | 0,090 | 50 | CQ05S8F1800T5E | 0,026 | 100 |  | 2 | Farnell | 0,007 € | 2 | 0,014
18 | 1 | 47K | 0805 | R3 | 2447664 | MCWR08X4702FTL | 0,009 | 10 | RHM47KKCT-ND | 0,036 | 10 | 603-RC0805FR-0747KL | 0,014 | 10 | 679-1434 | CRCW080547K0FKEA | 0,036 | 50 | RC0805FR-0747K | 0,022 | 100 |  | 1 | Farnell | 0,009 € | 1 | 0,009
19 | 2 | 4K7 | 0805 | R5, R11 | 2861530 | CRGCQ0805F4K7 | 0,012 | 10 | 311-4.70KCRCT-ND | 0,040 | 10 | 603-RC0805FR-074K7L | 0,027 | 10 | 223-0528 | CRG0805F4K7 | 0,023 | 50 | 0805S8F4701T5E | 0,023 | 100 |  | 2 | Farnell | 0,012 € | 2 | 0,023
20 | 2 | 47R | 0805 | R7, R13 | 2861899 | CRGCQ0805J47R | 0,007 | 10 | P47.0CCT-ND | 0,069 | 10 | 279-CRGCQ0805F47R | 0,028 | 10 | 223-0253 | CRG0805F47R | 0,016 | 50 | SMD0805-47R-1% | 0,022 | 100 |  | 2 | Farnell | 0,007 € | 2 | 0,013
21 | 1 | DR1206-33R-4/8 | 1206 resistor array | RN1 | 1770128 | CAY16-330J4LF | 0,069 | 10 | CAY16-330J4LFCT-ND | 0,090 | 1 | 652-CAY16-330J4LF | 0,085 | 1 | 522-5670 | CAY16-330J4LF | 0,004 | 50 | 4D03WGJ0330T | 0,009 | 100 |  | 1 | RS | 0,004 € | 1 | 0,004
22 | 7 | DR1206-47K-4/8 | 1206 resistor array | RN2, RN3, RN4, RN5, RN6, RN7, RN8 | 2787793 | CAY16-4702F4LF | 0,178 | 10 | CAY16-473J4LF | 0,080 | 10 | 652-CAY16-473J4LF | 0,016 | 10 | 522-5759 | CAY16-473J4LF | 0,020 | 50 | 4D03WGJ0473T | 0,013 | 100 |  | 7 | TME | 0,013 € | 7 | 0,091
23 | 2 | PESD12VL1BA,115 | SOD-323 | TVS1, TVS2 | 8737363 | PESD12VL1BA,115 | 0,365 | 5 | 1727-3808-1-ND | 0,320 | 10 | 771-PESD12VL1BA-T/R | 0,296 | 10 | 508-024 | PESD12VL1BA,115 | 0,294 | 20 | PESD12VL1BA.115 | 0,126 | 5 |  | 2 | TME | 0,126 € | 2 | 0,252
24 | 1 | 77317-104-28LF | THT, 28-pin 0.1" header right angled | X2 | - |  |  |  | S2111EC-14-ND | 1,030 | 1 | 649-77317-104-28LF | 1,540 | 1 | - |  |  |  | - |  |  | 1 |  | Digikey | 1,030 € | 1 | 1,030
25 | 2 | 691327310016 | THT, 16-pin 3.81mm terminal block header, male pins | X3, X4 | 1793077 | MCD 1,5/ 8-G1-3,81 | 5,770 | 1 | 732-691327310016-ND | 7,810 | 1 | 651-1843130 | 9,270 | 1 | 191-1724 | 691327310016 | 7,900 | 1 | - |  |  | 2 |  | Farnell | 5,770 € | 2 | 11,540
26 | 2 | DS1014-10RF1B | THT, 10-pin 2mm IDC, right angle | X6, X7 | - |  |  |  | 2BHR-10-HUA | 0,650 | 1 | - |  |  | - |  |  |  | DS1014-10RF1B | 0,220 | 3 | 2 |  | TME | 0,220 € | 2 | 0,440
27 | 5 | MM3Z18VT1G | SOD-323 | ZD1, ZD2, ZD3, ZD4, ZD5 | 1431193 | MM3Z18VT1G | 0,109 | 10 | MM3Z18VT1GOSCT-ND | 0,103 | 10 | 863-MM3Z18VT1G | 0,108 | 10 | 802-4574 | MM3Z18VT1G | 0,038 | 200 | MM3Z18VT1G | 0,025 | 25 |  | 5 | TME | 0,025 € | 5 | 0,126
 |  |  |  |  |  |  |  |  |  |  |  |  |  |  |  |  |  |  |  |  |  | 6 | 126 |  |  |  | 39,31 €
 |  | Not installed
 | 1 | N.C. |  | X1 |  |  |  |  |  |  |  |  |  |  |  |  |  |  |  |  |  |  | 1 | Farnell | 0,000 € | 1 | 0,000
 |  | Related parts and accessories
 | 2 | PMB-1 | PCB bracket; polyamide | KK1, KK2 | - |  |  |  | - |  |  | - |  |  | - |  |  |  | PMB-1 | 0,072 | 10 |  |  | TME | 0,072 € | 2 | 0,145
 | 4 | TJ0831530000G | 8-pin 3.81mm pluggable terminal block |  | 2579776 | EBK-08-B | 2,400 | 1 | 609-3803-ND | 1,760 | 1 | 649-220004-D081B01LF | 1,530 | 1 | - |  |  |  | 15EDGK-3.81-08P-14-00A(H) | 1,430 | 1 |  |  | TME | 1,430 € | 4 | 5,720
 |  |  |  |  |  |  |  |  |  |  |  |  |  |  |  |  |  |  |  |  |  |  |  |  |  |  | 5,86 €
 |  | Custom made components
 | 1 | PCB 2-layer 146 x 95 mm |  | - |  |  |  |  |  |  |  |  |  |  |  |  |  |  |  |  |  |  |  | JLCPCB | 6,244 € | 1 | 6,244
 |  |  |  |  |  |  |  |  |  |  |  |  |  |  |  |  |  |  |  |  |  |  |  |  |  |  | 6,24 €
 |  |  | All prices are net prices (without VAT)
 |  |  |  |  |  |  |  |  |  |  |  |  |  |  |  |  |  |  |  |  |  |  |  |  |  | Total | 51,42 €
 |  |  | Please note that BOM does not contain ordering number for parts on reels or that which includes re-reeling fee (e.g. Farnell). Take also into account that total cost is higher because min. quantity (MOQ) for many parts is larger then what is needed for single unit.
 |  |  | All resistors are 1% 0805 and all capacitors are X7R 0805 if not otherwise specified.

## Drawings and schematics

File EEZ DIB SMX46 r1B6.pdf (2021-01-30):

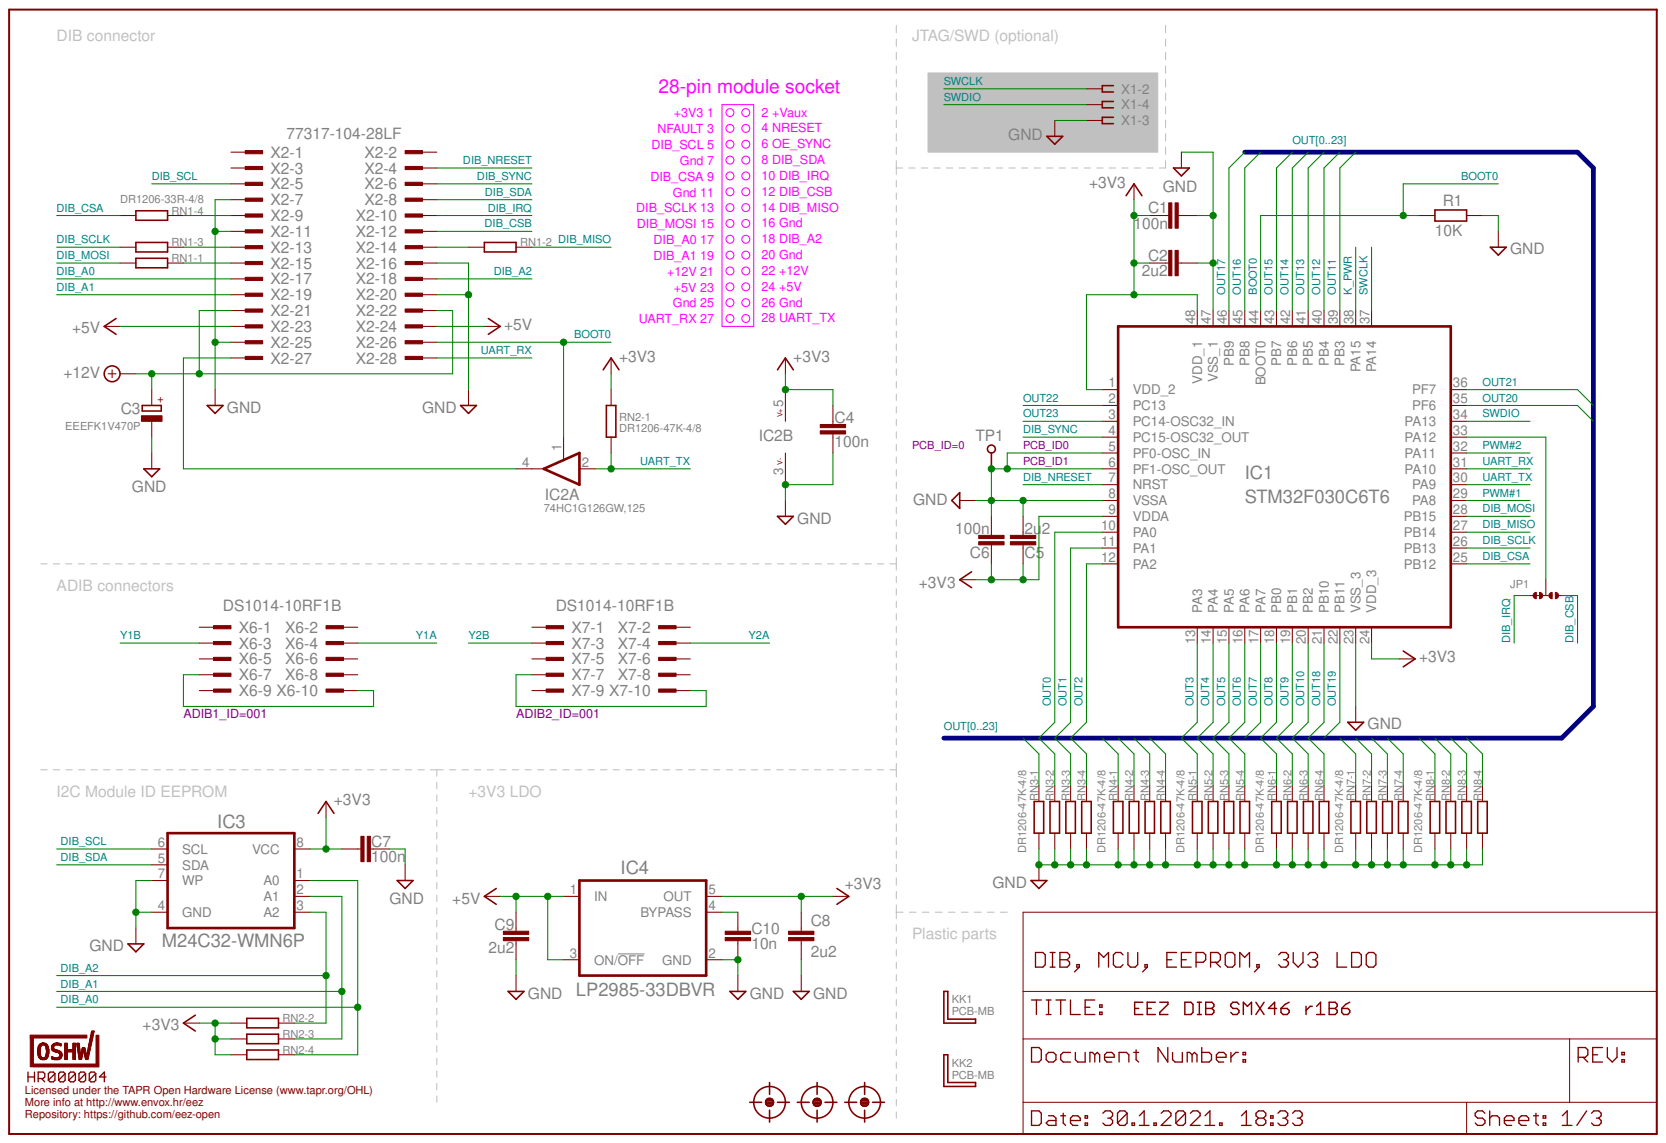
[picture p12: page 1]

Licensed under the TAPR Open Hardware License (www.tapr.org/OHL) Repository: https://github.com/eez-open More info at http://www.envox.hr/eez

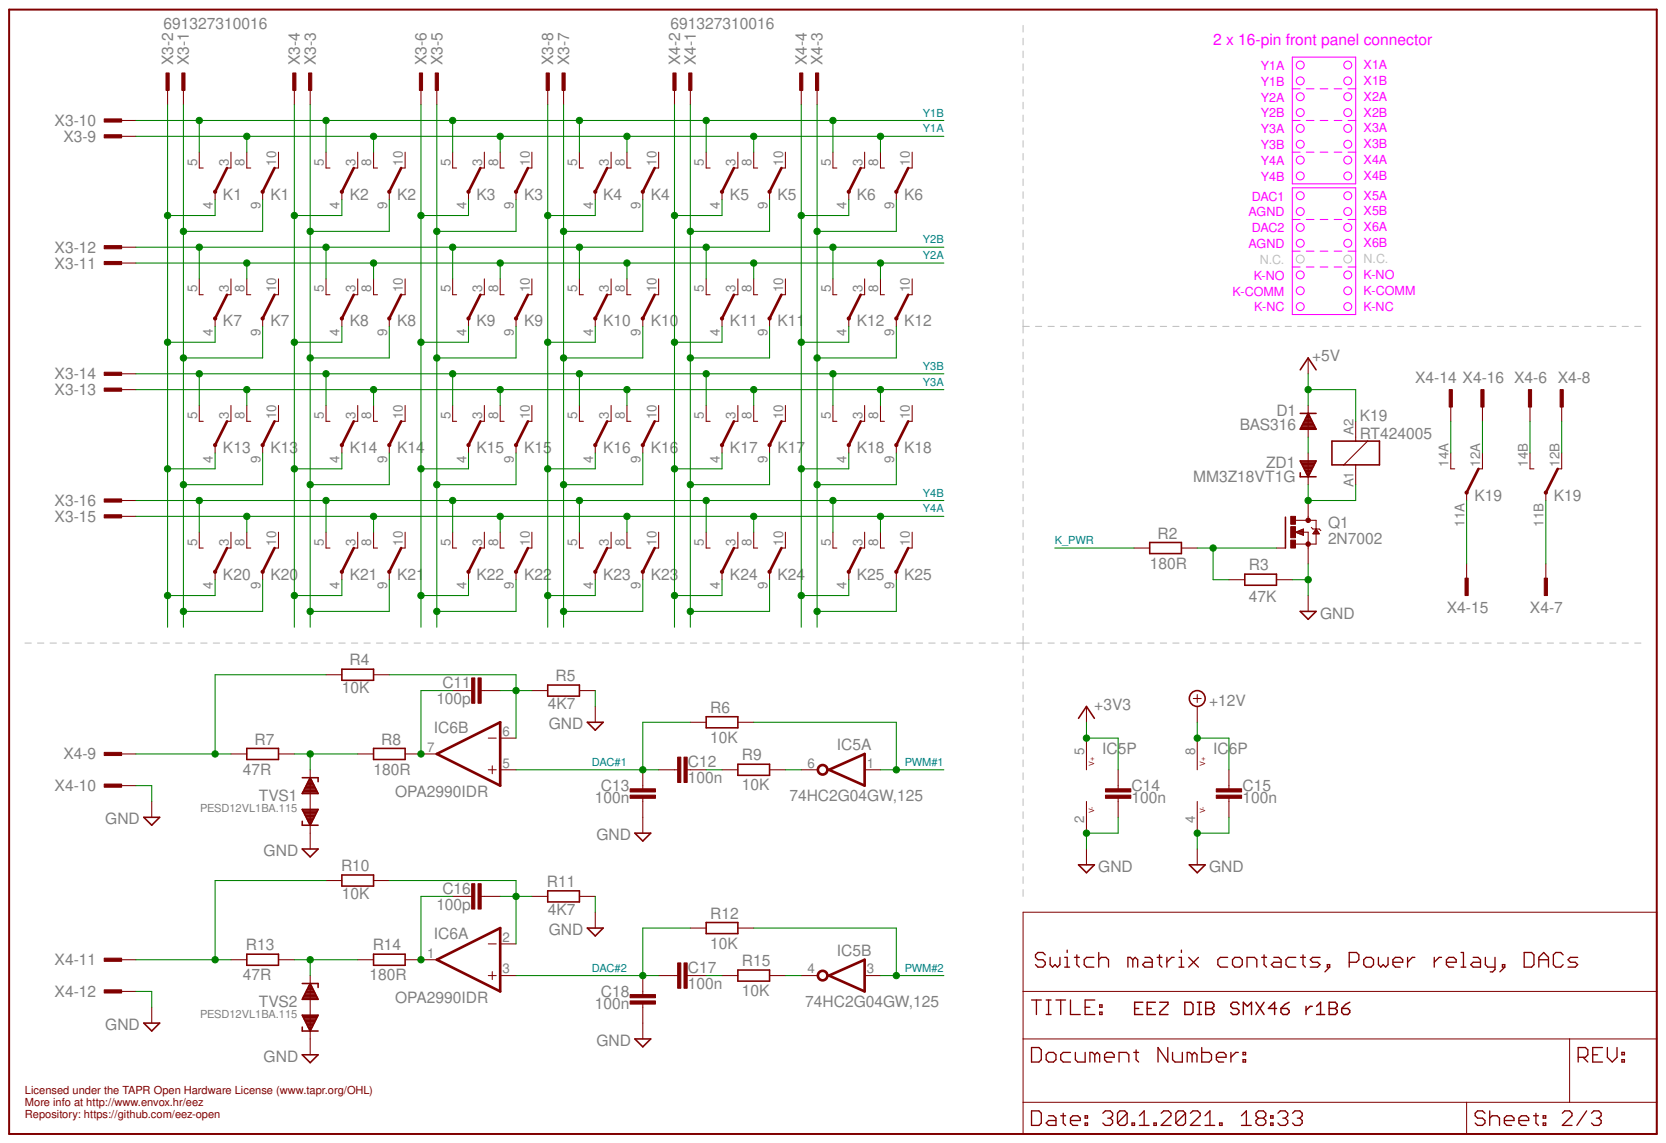
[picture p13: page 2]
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

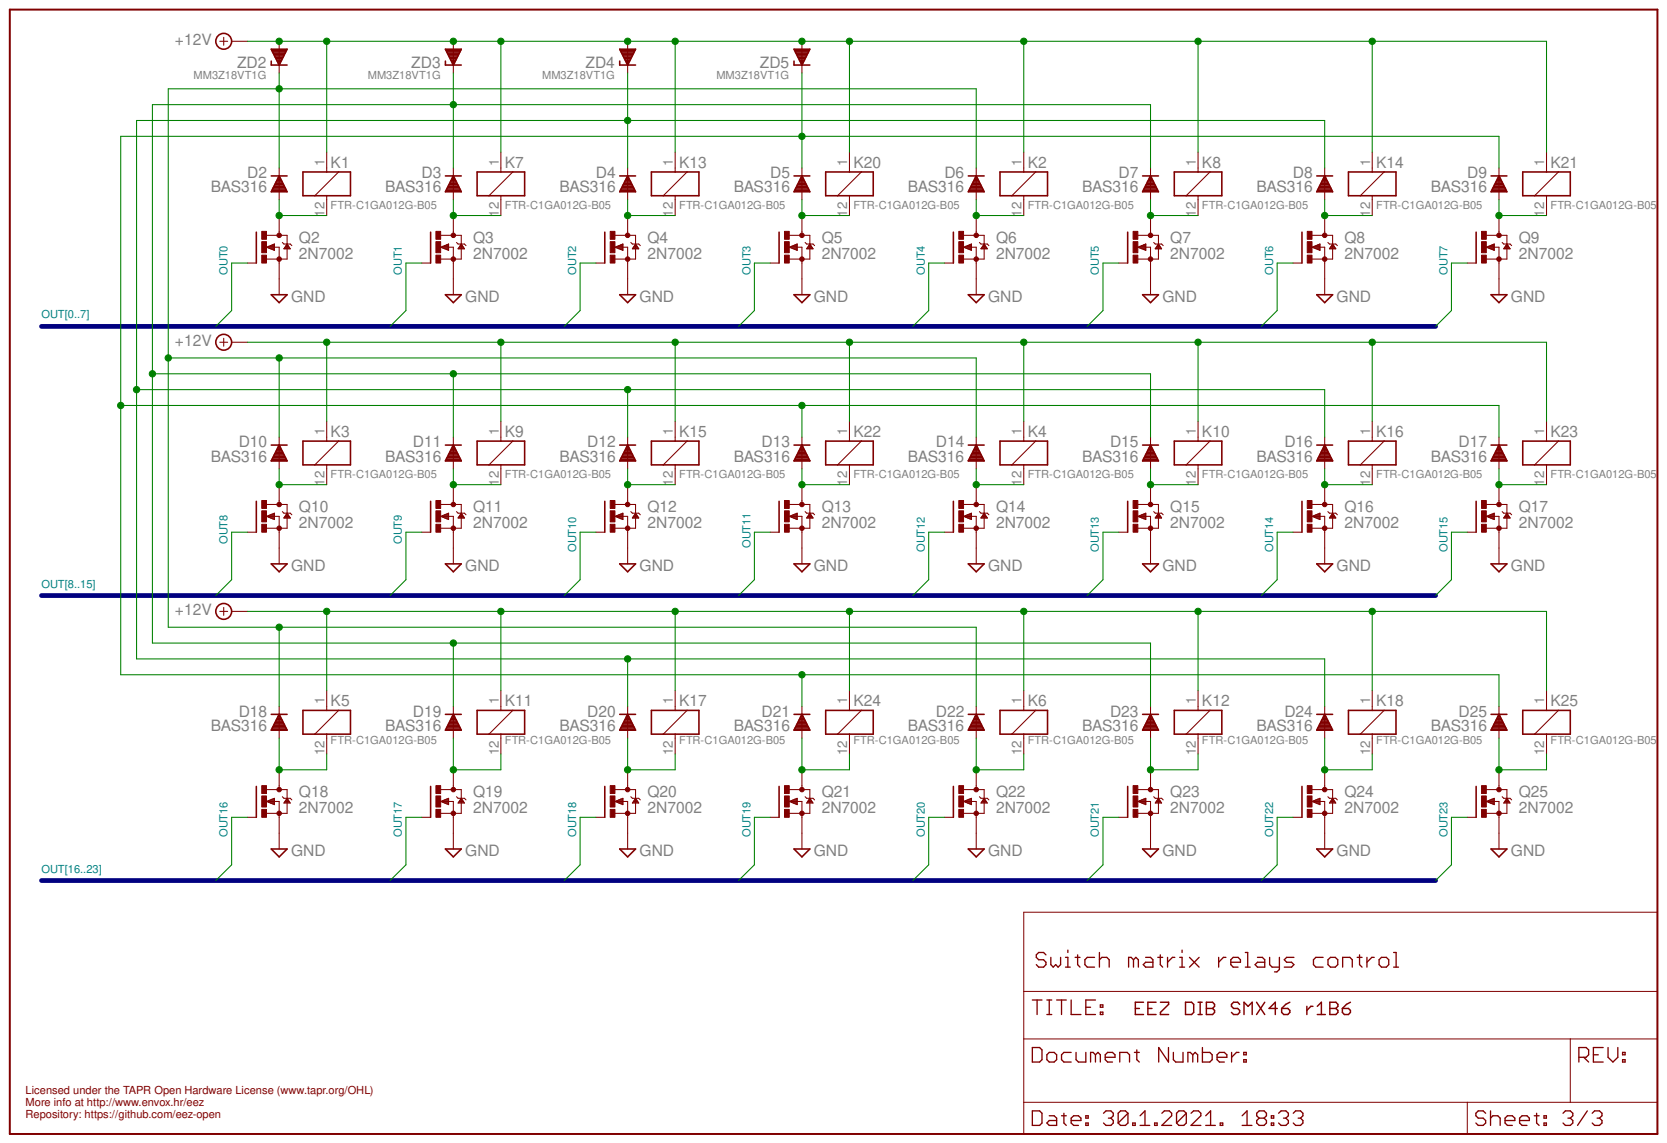
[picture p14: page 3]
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

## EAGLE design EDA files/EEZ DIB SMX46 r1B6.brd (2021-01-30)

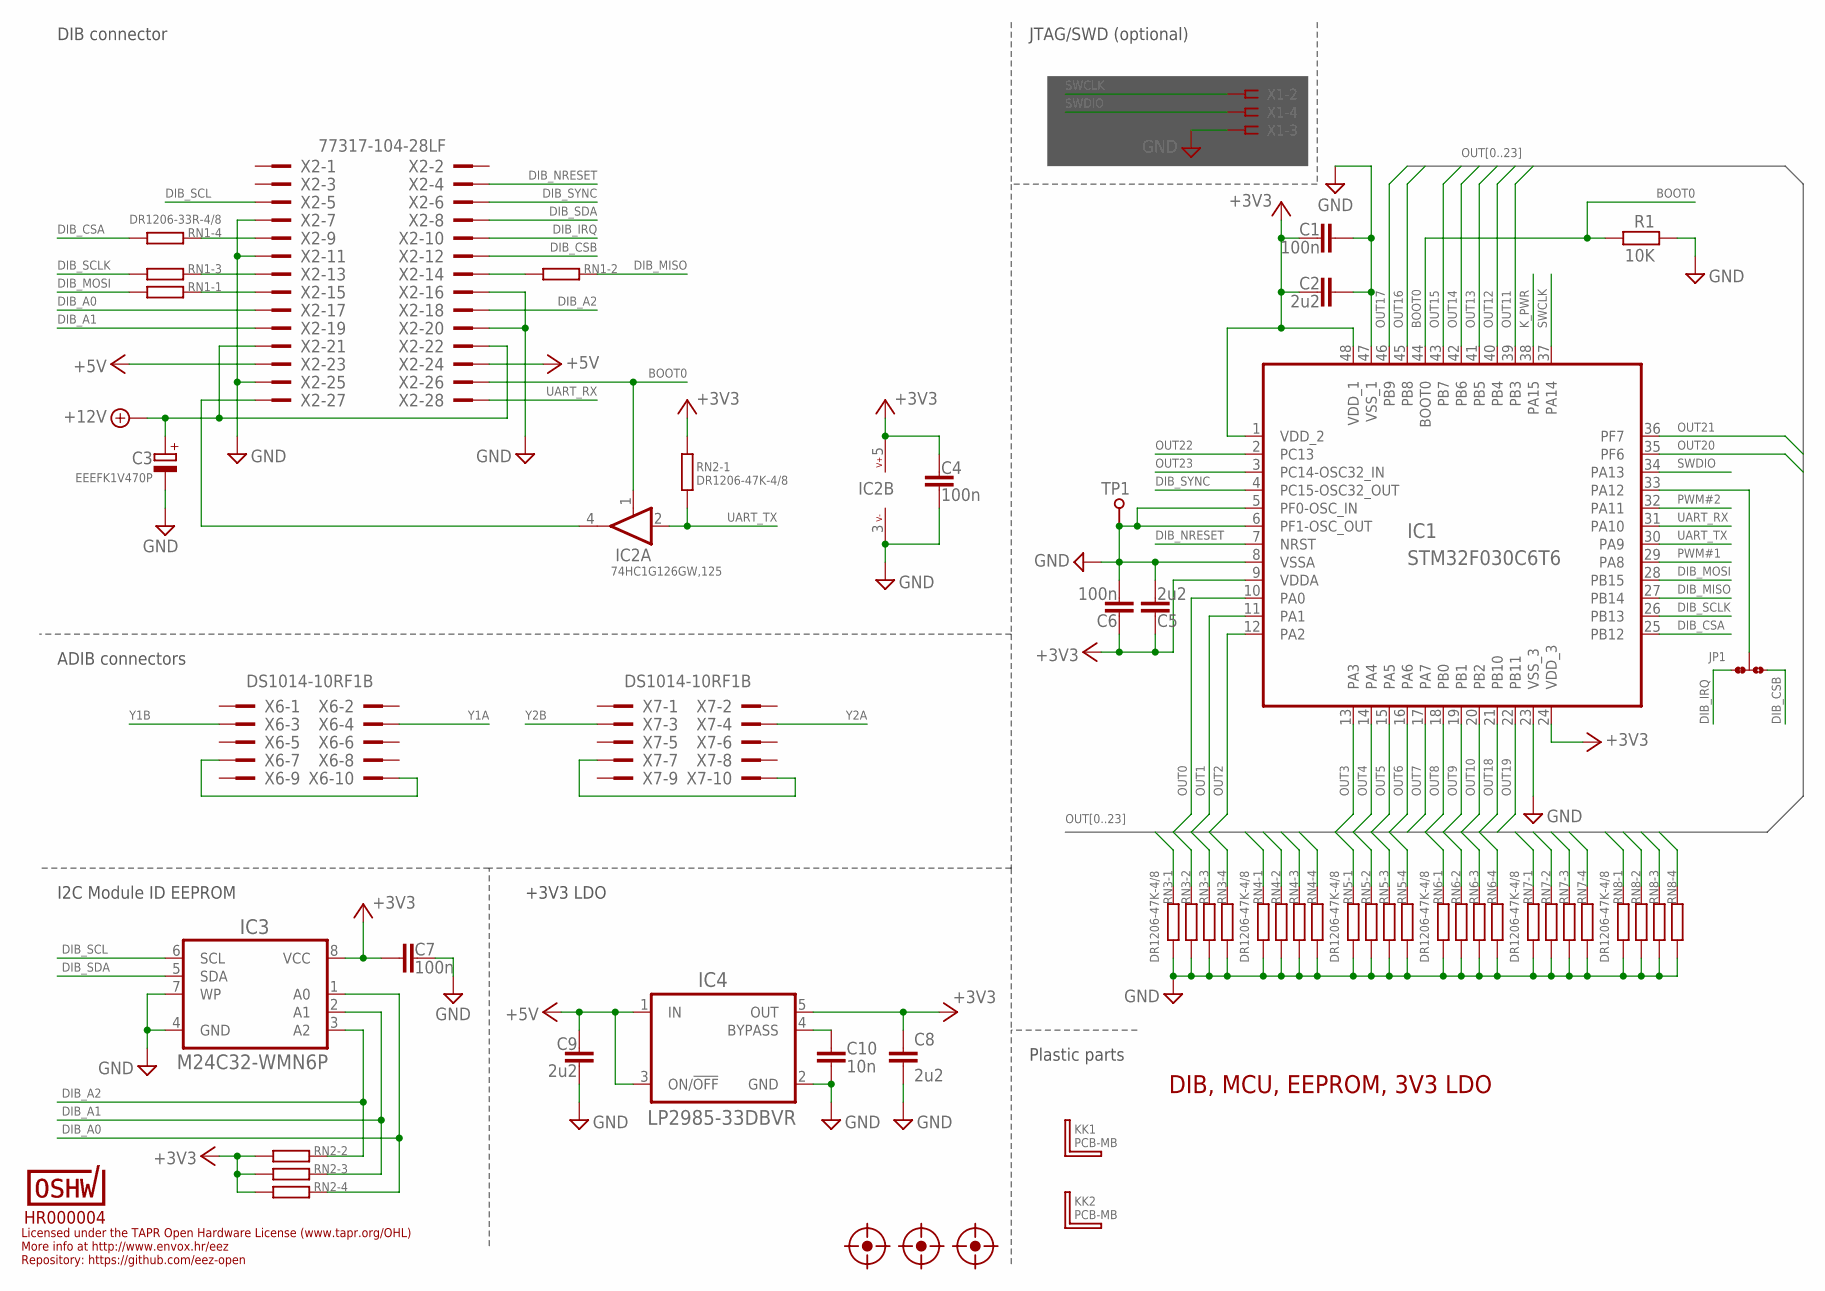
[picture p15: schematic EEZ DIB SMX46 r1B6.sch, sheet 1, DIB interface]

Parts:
C1, C4, C6, C7: 100n; C0603
C2, C5, C8, C9: 2u2; C0805
C3: EEEFK1V470P; CAPAE660X610N
C10: 10n; C0805
FM1, FM2, FM3: FIDUCIAL_2; FIDUCIAL_DUAL
IC1: STM32F030C6T6; LQFP-48
IC2: 74HC1G126GW,125; SOT65P210X110-5N
IC3: M24C32-WMN6P; SOIC127P600X173-8N
IC4: LP2985-33DBVR; SOT95P270X145-5N
JP1: JP3-CUT-0805-ROTATED; JP3-0805-CUT2
KK1, KK2: PCB-MB
R1: 10K; R0805
RN1: DR1206-33R-4/8; CAY16
RN2, RN3, RN4, RN5, RN6, RN7, RN8: DR1206-47K-4/8; CAY16
TP1: PCB_TEST_TABSHIELD; PCB_SHIELD_TAB
U$3: HR000004; CERT-SMALL-SILK
X1: N.C.; SSW-106-02-S-S
X2: 77317-104-28LF
X6, X7: DS1014-10RF1B

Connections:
+3V3: C1.2, C2.1, C4.1, C5.2, C6.1, C7.2, C8.1, IC1.1 (VDD_2), IC1.9 (VDDA), IC1.24 (VDD_3), IC1.48 (VDD_1), IC2.5 (V+), IC3.8 (VCC), IC4.5 (OUT), RN2.5 (2), RN2.6 (2), RN2.7 (2), RN2.8 (2); also elsewhere on the board
+5V: C9.2, IC4.1 (IN), IC4.3 (ON/!OFF), X2.23, X2.24; also elsewhere on the board
+12V: C3.1 (+), X2.21, X2.22; also elsewhere on the board
BOOT0: IC1.44 (BOOT0), IC2.1 (EN), R1.2, X2.26
DIB_A0: IC3.1 (A0), RN2.4 (1), X2.17
DIB_A1: IC3.2 (A1), RN2.3 (1), X2.19
DIB_A2: IC3.3 (A2), RN2.2 (1), X2.18
DIB_CSA: IC1.25 (PB12), RN1.4 (1)
DIB_CSB: JP1.NO, X2.12
DIB_IRQ: JP1.NC, X2.10
DIB_MISO: IC1.27 (PB14), RN1.2 (1)
DIB_MOSI: IC1.28 (PB15), RN1.1
DIB_NRESET: IC1.7 (NRST), X2.4
DIB_SCL: IC3.6 (SCL), X2.5
DIB_SCLK: IC1.26 (PB13), RN1.3 (1)
DIB_SDA: IC3.5 (SDA), X2.8
DIB_SYNC: IC1.4 (PC15-OSC32_OUT), X2.6
GND: C1.1, C2.2, C3.2 (-), C4.2, C5.1, C6.2, C7.1, C8.2, C9.1, C10.1, IC1.5 (PF0-OSC_IN), IC1.6 (PF1-OSC_OUT), IC1.8 (VSSA), IC1.23 (VSS_3), IC1.47 (VSS_1), IC2.3 (V-), IC3.4 (GND), IC3.7 (WP), IC4.2 (GND), R1.1, RN3.1, RN3.2 (1), RN3.3 (1), RN3.4 (1), RN4.1, RN4.2 (1), RN4.3 (1), RN4.4 (1), RN5.1, RN5.2 (1), RN5.3 (1), RN5.4 (1), RN6.1, RN6.2 (1), RN6.3 (1), RN6.4 (1), RN7.3 (1), RN7.4 (1), RN7.7 (2), RN7.8 (2), RN8.3 (1), RN8.4 (1), RN8.7 (2), RN8.8 (2), TP1.1, X1.3, X2.7, X2.11, X2.16, X2.20, X2.25; also elsewhere on the board
K_PWR: IC1.38 (PA15); also elsewhere on the board
unnamed: X6.7, X6.10
unnamed: X7.7, X7.10
unnamed: RN1.5 (2), X2.9
unnamed: C10.2, IC4.4 (BYPASS)
unnamed: IC2.4 (O), X2.27
unnamed: IC1.33 (PA12), JP1.COM
unnamed: RN1.6 (2), X2.13
unnamed: RN1.7 (2), X2.14
unnamed: RN1.8 (2), X2.15
OUT0: IC1.10 (PA0), RN3.8 (2); also elsewhere on the board
OUT1: IC1.11 (PA1), RN3.7 (2); also elsewhere on the board
OUT2: IC1.12 (PA2), RN6.8 (2); also elsewhere on the board
OUT3: IC1.13 (PA3), RN6.7 (2); also elsewhere on the board
OUT4: IC1.14 (PA4), RN3.5 (2); also elsewhere on the board
OUT5: IC1.15 (PA5), RN3.6 (2); also elsewhere on the board
OUT6: IC1.16 (PA6), RN6.5 (2); also elsewhere on the board
OUT7: IC1.17 (PA7), RN6.6 (2); also elsewhere on the board
OUT8: IC1.18 (PB0), RN4.7 (2); also elsewhere on the board
OUT9: IC1.19 (PB1), RN4.8 (2); also elsewhere on the board
OUT10: IC1.20 (PB2), RN7.6 (2); also elsewhere on the board
OUT11: IC1.39 (PB3), RN7.5 (2); also elsewhere on the board
OUT12: IC1.40 (PB4), RN4.5 (2); also elsewhere on the board
OUT13: IC1.41 (PB5), RN4.6 (2); also elsewhere on the board
OUT14: IC1.42 (PB6), RN7.2 (1); also elsewhere on the board
OUT15: IC1.43 (PB7), RN7.1; also elsewhere on the board
OUT16: IC1.45 (PB8), RN5.7 (2); also elsewhere on the board
OUT17: IC1.46 (PB9), RN5.8 (2); also elsewhere on the board
OUT18: IC1.21 (PB10), RN8.5 (2); also elsewhere on the board
OUT19: IC1.22 (PB11), RN8.6 (2); also elsewhere on the board
OUT20: IC1.35 (PF6), RN5.5 (2); also elsewhere on the board
OUT21: IC1.36 (PF7), RN5.6 (2); also elsewhere on the board
OUT22: IC1.2 (PC13), RN8.1; also elsewhere on the board
OUT23: IC1.3 (PC14-OSC32_IN), RN8.2 (1); also elsewhere on the board
PWM#1: IC1.29 (PA8); also elsewhere on the board
PWM#2: IC1.32 (PA11); also elsewhere on the board
SWCLK: IC1.37 (PA14), X1.2
SWDIO: IC1.34 (PA13), X1.4
UART_RX: IC1.31 (PA10), X2.28
UART_TX: IC1.30 (PA9), IC2.2 (I), RN2.1
Y1A: X6.4; also elsewhere on the board
Y1B: X6.3; also elsewhere on the board
Y2A: X7.4; also elsewhere on the board
Y2B: X7.3; also elsewhere on the board

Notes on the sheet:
Licensed under the TAPR Open Hardware License (www.tapr.org/OHL)
Repository: https://github.com/eez-open
More info at http://www.envox.hr/eez
DIB, MCU, EEPROM, 3V3 LDO
Plastic parts
I2C Module ID EEPROM
+3V3 LDO
JTAG/SWD (optional)
DIB connector
ADIB connectors

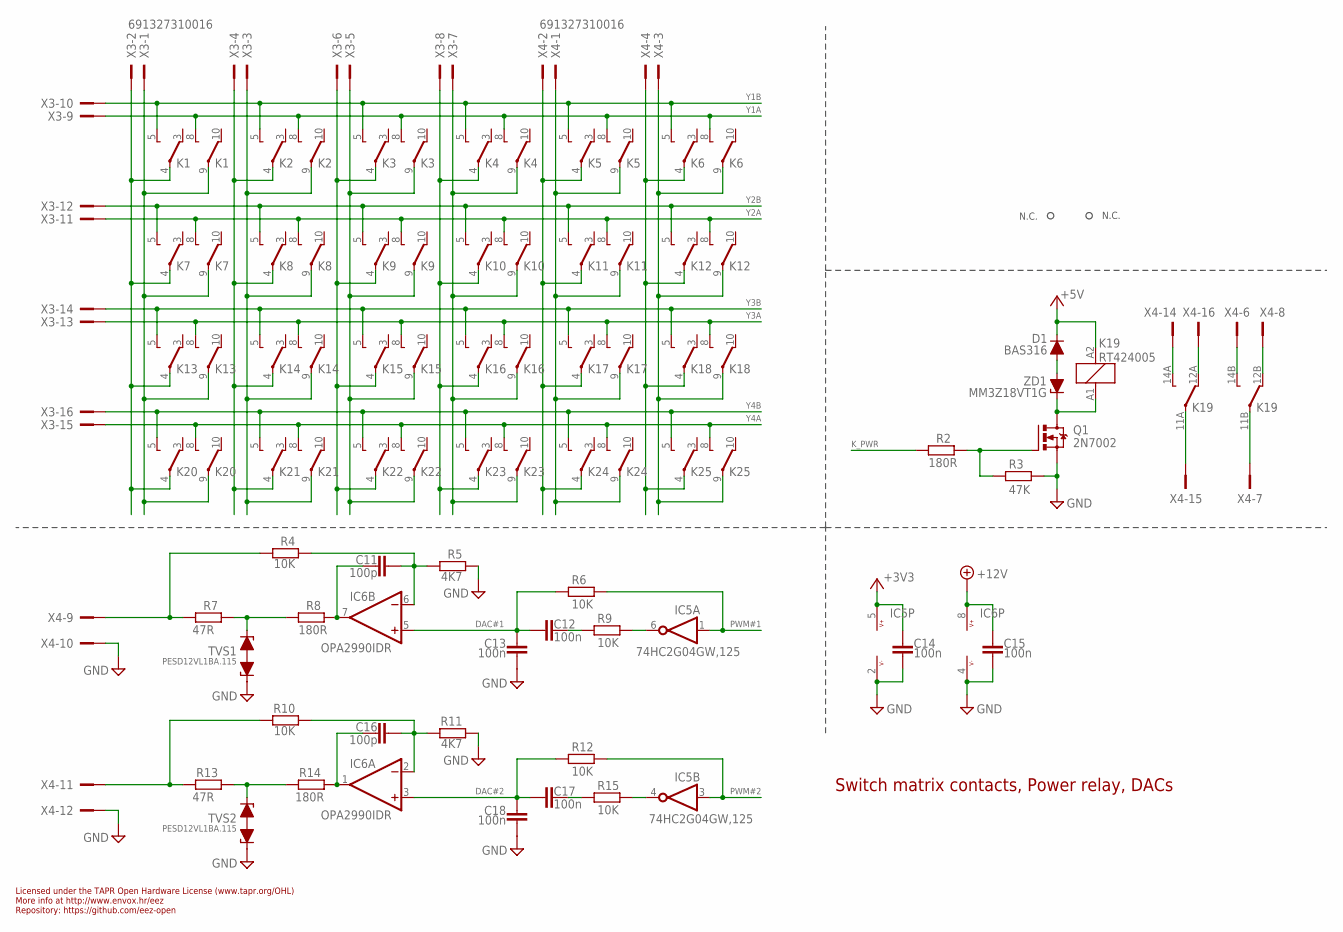
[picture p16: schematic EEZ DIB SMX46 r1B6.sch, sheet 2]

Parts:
C11, C16: 100p; C0805
C12, C13, C14, C15, C17, C18: 100n; C0603
D1: BAS316; SOD323-R
IC5: 74HC2G04GW,125; SOT65P210X110-6N
IC6: OPA2990IDR; SOIC127P600X173-8N
K1, K2, K3, K4, K5, K6, K7, K8, K9, K10, K11, K12, K13, K14, K15, K16, K17, K18, K20, K21, K22, K23, K24, K25: FTR-C1GA012G-B05; FTR-C1
K19: RT424005; RT-C/016A5_ROUND
Q1: 2N7002; SOT103P240X110-3N; MPN 2N7002-7-F
R2, R8, R14: 180R; R0805
R3: 47K; R0805
R4, R6, R9, R10, R12, R15: 10K; R0805
R5, R11: 4K7; R0805
R7, R13: 47R; R0805
TVS1, TVS2: PESD12VL1BA.115; SOD323-BIDIR
X3, X4: 691327310016
ZD1: MM3Z18VT1G; SOD323-R

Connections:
+3V3: C14.1, IC5.5 (V+); also elsewhere on the board
+5V: D1.C, K19.A2 (C1); also elsewhere on the board
+12V: C15.1, IC6.8 (V+); also elsewhere on the board
DAC#1: C12.1, C13.1, IC6.5 (+IN), R6.1
DAC#2: C17.1, C18.1, IC6.3 (+IN), R12.1
GND: C13.2, C14.2, C15.2, C18.2, IC5.2 (V-), IC6.4 (V-), Q1.2 (S), R3.1, R5.1, R11.1, TVS1.1, TVS2.1, X4.10, X4.12; also elsewhere on the board
ISET1: R7.1, R8.2, TVS1.2
ISET2: R13.1, R14.2, TVS2.2
K_PWR: R2.2; also elsewhere on the board
unnamed: K1.4, K7.4, K13.4, K20.4, X3.2
unnamed: K1.9, K7.9, K13.9, K20.9, X3.1
unnamed: K5.4, K11.4, K17.4, K24.4, X4.2
unnamed: K2.4, K8.4, K14.4, K21.4, X3.4
unnamed: K2.9, K8.9, K14.9, K21.9, X3.3
unnamed: K5.9, K11.9, K17.9, K24.9, X4.1
unnamed: K6.4, K12.4, K18.4, K25.4, X4.4
unnamed: K6.9, K12.9, K18.9, K25.9, X4.3
unnamed: K3.4, K9.4, K15.4, K22.4, X3.6
unnamed: K3.9, K9.9, K15.9, K22.9, X3.5
unnamed: K4.4, K10.4, K16.4, K23.4, X3.8
unnamed: K4.9, K10.9, K16.9, K23.9, X3.7
unnamed: R4.2, R7.2, X4.9
unnamed: C17.2, R15.1
unnamed: IC5.4 (O), R15.2
unnamed: C11.1, IC6.7 (OUT), R8.1
unnamed: C16.2, IC6.2 (-IN), R10.1, R11.2
unnamed: Q1.1 (G), R2.1, R3.2
unnamed: C16.1, IC6.1 (OUT), R14.1
unnamed: K19.11B, X4.7
unnamed: K19.12B (S), X4.8
unnamed: R10.2, R13.2, X4.11
unnamed: K19.14B (O), X4.6
unnamed: K19.11A, X4.15
unnamed: K19.12A (S), X4.16
unnamed: K19.14A (O), X4.14
unnamed: D1.A, ZD1.A
unnamed: K19.A1 (C2), Q1.3 (D), ZD1.C
unnamed: C12.2, R9.1
unnamed: C11.2, IC6.6 (-IN), R4.1, R5.2
unnamed: IC5.6 (O), R9.2
PWM#1: IC5.1 (I), R6.2; also elsewhere on the board
PWM#2: IC5.3 (I), R12.2; also elsewhere on the board
Y1A: K1.8 (O), K2.8 (O), K3.8 (O), K4.8 (O), K5.8 (O), K6.8 (O), X3.9; also elsewhere on the board
Y1B: K1.5 (O), K2.5 (O), K3.5 (O), K4.5 (O), K5.5 (O), K6.5 (O), X3.10; also elsewhere on the board
Y2A: K7.8 (O), K8.8 (O), K9.8 (O), K10.8 (O), K11.8 (O), K12.8 (O), X3.11; also elsewhere on the board
Y2B: K7.5 (O), K8.5 (O), K9.5 (O), K10.5 (O), K11.5 (O), K12.5 (O), X3.12; also elsewhere on the board
Y3A: K13.8 (O), K14.8 (O), K15.8 (O), K16.8 (O), K17.8 (O), K18.8 (O), X3.13
Y3B: K13.5 (O), K14.5 (O), K15.5 (O), K16.5 (O), K17.5 (O), K18.5 (O), X3.14
Y4A: K20.8 (O), K21.8 (O), K22.8 (O), K23.8 (O), K24.8 (O), K25.8 (O), X3.15
Y4B: K20.5 (O), K21.5 (O), K22.5 (O), K23.5 (O), K24.5 (O), K25.5 (O), X3.16

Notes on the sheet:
Licensed under the TAPR Open Hardware License (www.tapr.org/OHL)
Repository: https://github.com/eez-open
More info at http://www.envox.hr/eez
Switch matrix contacts, Power relay, DACs
N.C.

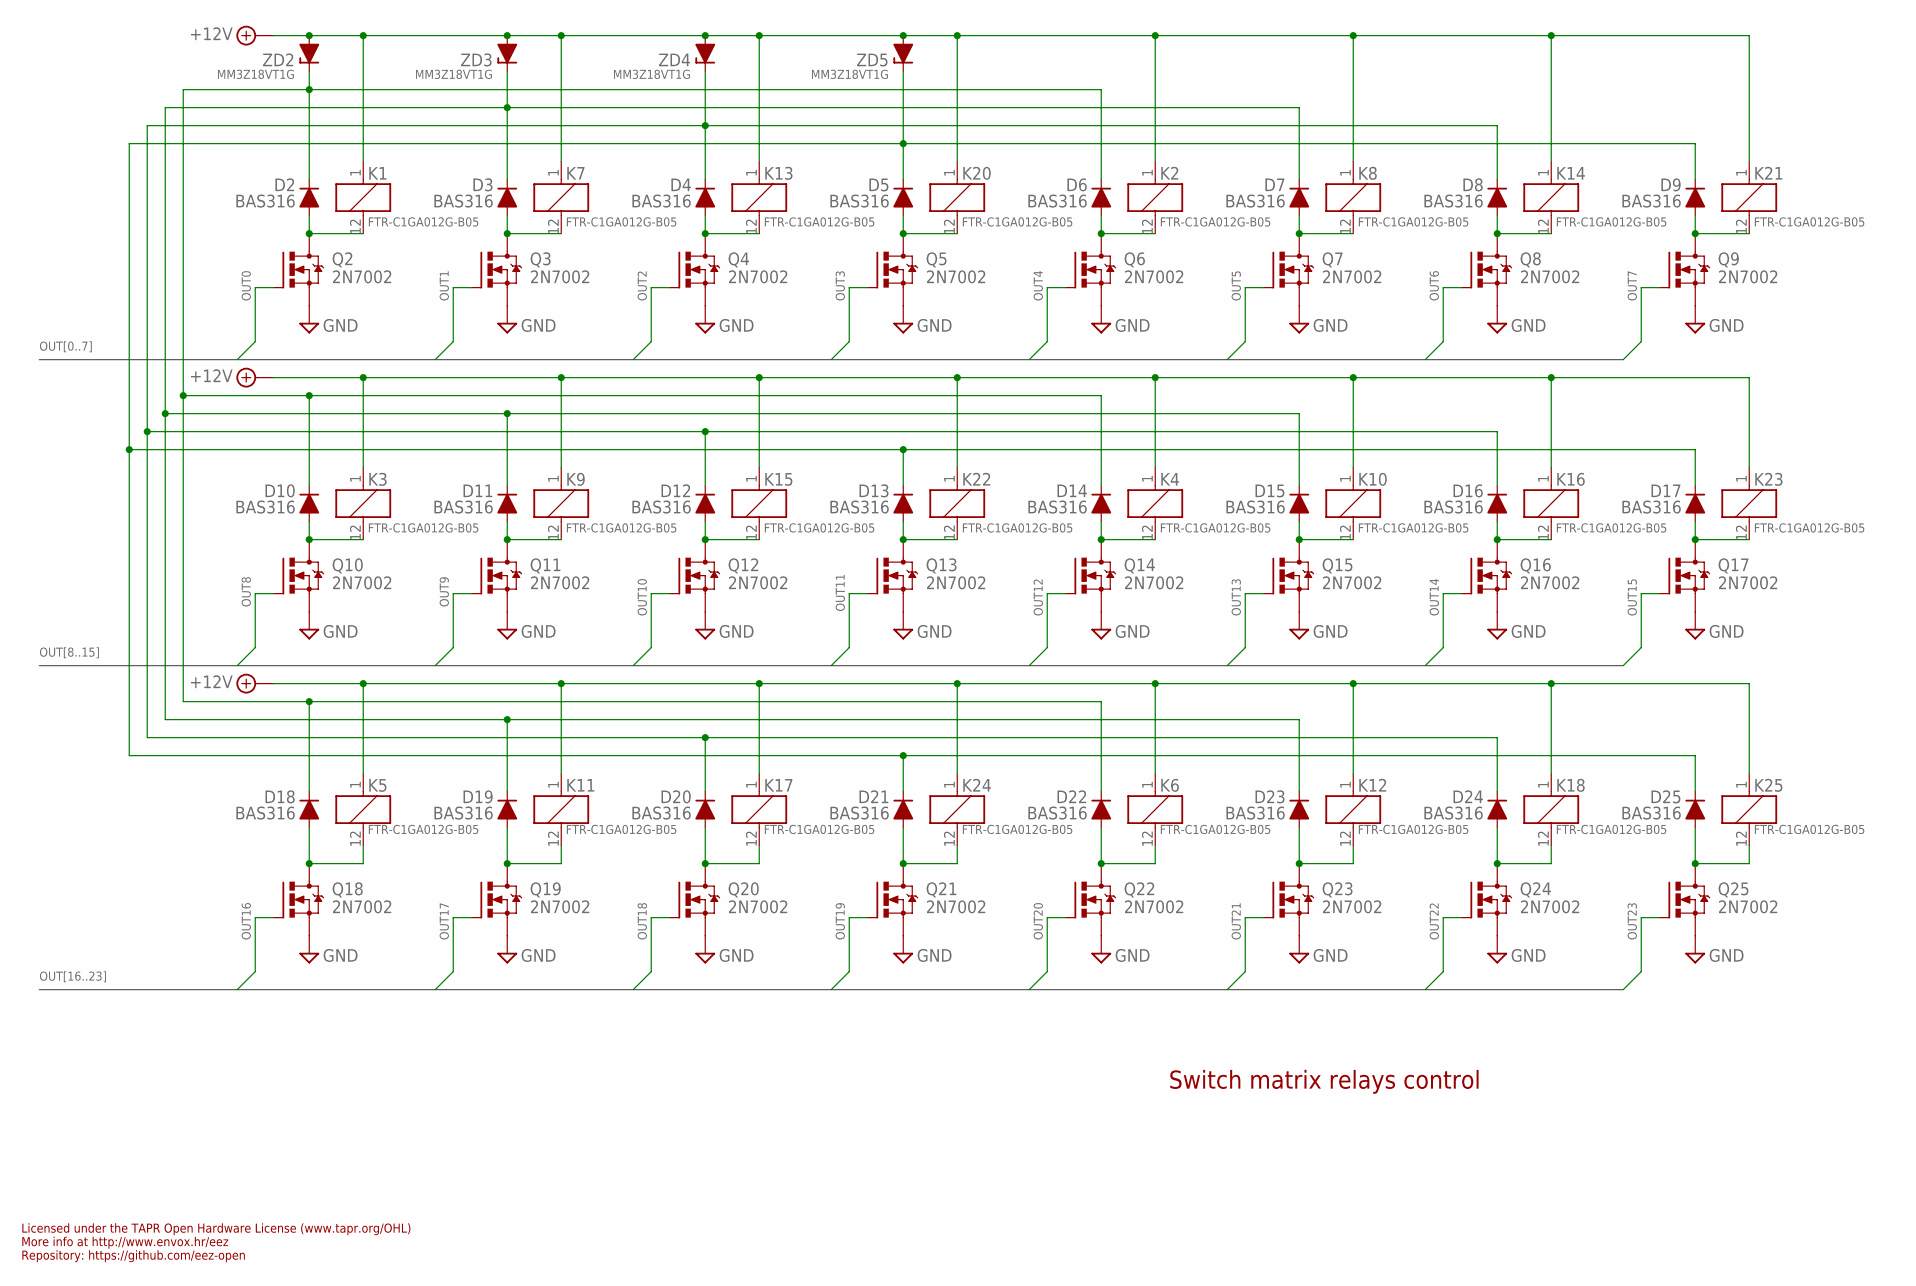
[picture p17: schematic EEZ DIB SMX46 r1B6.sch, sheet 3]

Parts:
D2, D3, D4, D5, D6, D7, D8, D9, D10, D11, D12, D13, D14, D15, D16, D17, D18, D19, D20, D21, D22, D23, D24, D25: BAS316; SOD323-R
K1, K2, K3, K4, K5, K6, K7, K8, K9, K10, K11, K12, K13, K14, K15, K16, K17, K18, K20, K21, K22, K23, K24, K25: FTR-C1GA012G-B05; FTR-C1
Q2, Q3, Q4, Q5, Q6, Q7, Q8, Q9, Q10, Q11, Q12, Q13, Q14, Q15, Q16, Q17, Q18, Q19, Q20, Q21, Q22, Q23, Q24, Q25: 2N7002; SOT103P240X110-3N; MPN 2N7002-7-F
ZD2, ZD3, ZD4, ZD5: MM3Z18VT1G; SOD323-R

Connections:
+12V: K1.1 (C1), K2.1 (C1), K3.1 (C1), K4.1 (C1), K5.1 (C1), K6.1 (C1), K7.1 (C1), K8.1 (C1), K9.1 (C1), K10.1 (C1), K11.1 (C1), K12.1 (C1), K13.1 (C1), K14.1 (C1), K15.1 (C1), K16.1 (C1), K17.1 (C1), K18.1 (C1), K20.1 (C1), K21.1 (C1), K22.1 (C1), K23.1 (C1), K24.1 (C1), K25.1 (C1), ZD2.A, ZD3.A, ZD4.A, ZD5.A; also elsewhere on the board
GND: Q2.2 (S), Q3.2 (S), Q4.2 (S), Q5.2 (S), Q6.2 (S), Q7.2 (S), Q8.2 (S), Q9.2 (S), Q10.2 (S), Q11.2 (S), Q12.2 (S), Q13.2 (S), Q14.2 (S), Q15.2 (S), Q16.2 (S), Q17.2 (S), Q18.2 (S), Q19.2 (S), Q20.2 (S), Q21.2 (S), Q22.2 (S), Q23.2 (S), Q24.2 (S), Q25.2 (S); also elsewhere on the board
unnamed: D2.C, D6.C, D10.C, D14.C, D18.C, D22.C, ZD2.C
unnamed: D3.C, D7.C, D11.C, D15.C, D19.C, D23.C, ZD3.C
unnamed: D4.C, D8.C, D12.C, D16.C, D20.C, D24.C, ZD4.C
unnamed: D5.C, D9.C, D13.C, D17.C, D21.C, D25.C, ZD5.C
unnamed: D4.A, K13.12 (C2), Q4.3 (D)
unnamed: D8.A, K14.12 (C2), Q8.3 (D)
unnamed: D10.A, K3.12 (C2), Q10.3 (D)
unnamed: D9.A, K21.12 (C2), Q9.3 (D)
unnamed: D11.A, K9.12 (C2), Q11.3 (D)
unnamed: D7.A, K8.12 (C2), Q7.3 (D)
unnamed: D12.A, K15.12 (C2), Q12.3 (D)
unnamed: D6.A, K2.12 (C2), Q6.3 (D)
unnamed: D13.A, K22.12 (C2), Q13.3 (D)
unnamed: D3.A, K7.12 (C2), Q3.3 (D)
unnamed: D14.A, K4.12 (C2), Q14.3 (D)
unnamed: D2.A, K1.12 (C2), Q2.3 (D)
unnamed: D15.A, K10.12 (C2), Q15.3 (D)
unnamed: D5.A, K20.12 (C2), Q5.3 (D)
unnamed: D16.A, K16.12 (C2), Q16.3 (D)
unnamed: D17.A, K23.12 (C2), Q17.3 (D)
unnamed: D19.A, K11.12 (C2), Q19.3 (D)
unnamed: D20.A, K17.12 (C2), Q20.3 (D)
unnamed: D21.A, K24.12 (C2), Q21.3 (D)
unnamed: D22.A, K6.12 (C2), Q22.3 (D)
unnamed: D23.A, K12.12 (C2), Q23.3 (D)
unnamed: D18.A, K5.12 (C2), Q18.3 (D)
unnamed: D24.A, K18.12 (C2), Q24.3 (D)
unnamed: D25.A, K25.12 (C2), Q25.3 (D)
OUT0: Q2.1 (G); also elsewhere on the board
OUT1: Q3.1 (G); also elsewhere on the board
OUT2: Q4.1 (G); also elsewhere on the board
OUT3: Q5.1 (G); also elsewhere on the board
OUT4: Q6.1 (G); also elsewhere on the board
OUT5: Q7.1 (G); also elsewhere on the board
OUT6: Q8.1 (G); also elsewhere on the board
OUT7: Q9.1 (G); also elsewhere on the board
OUT8: Q10.1 (G); also elsewhere on the board
OUT9: Q11.1 (G); also elsewhere on the board
OUT10: Q12.1 (G); also elsewhere on the board
OUT11: Q13.1 (G); also elsewhere on the board
OUT12: Q14.1 (G); also elsewhere on the board
OUT13: Q15.1 (G); also elsewhere on the board
OUT14: Q16.1 (G); also elsewhere on the board
OUT15: Q17.1 (G); also elsewhere on the board
OUT16: Q18.1 (G); also elsewhere on the board
OUT17: Q19.1 (G); also elsewhere on the board
OUT18: Q20.1 (G); also elsewhere on the board
OUT19: Q21.1 (G); also elsewhere on the board
OUT20: Q22.1 (G); also elsewhere on the board
OUT21: Q23.1 (G); also elsewhere on the board
OUT22: Q24.1 (G); also elsewhere on the board
OUT23: Q25.1 (G); also elsewhere on the board

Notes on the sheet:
Licensed under the TAPR Open Hardware License (www.tapr.org/OHL)
Repository: https://github.com/eez-open
More info at http://www.envox.hr/eez
Switch matrix relays control

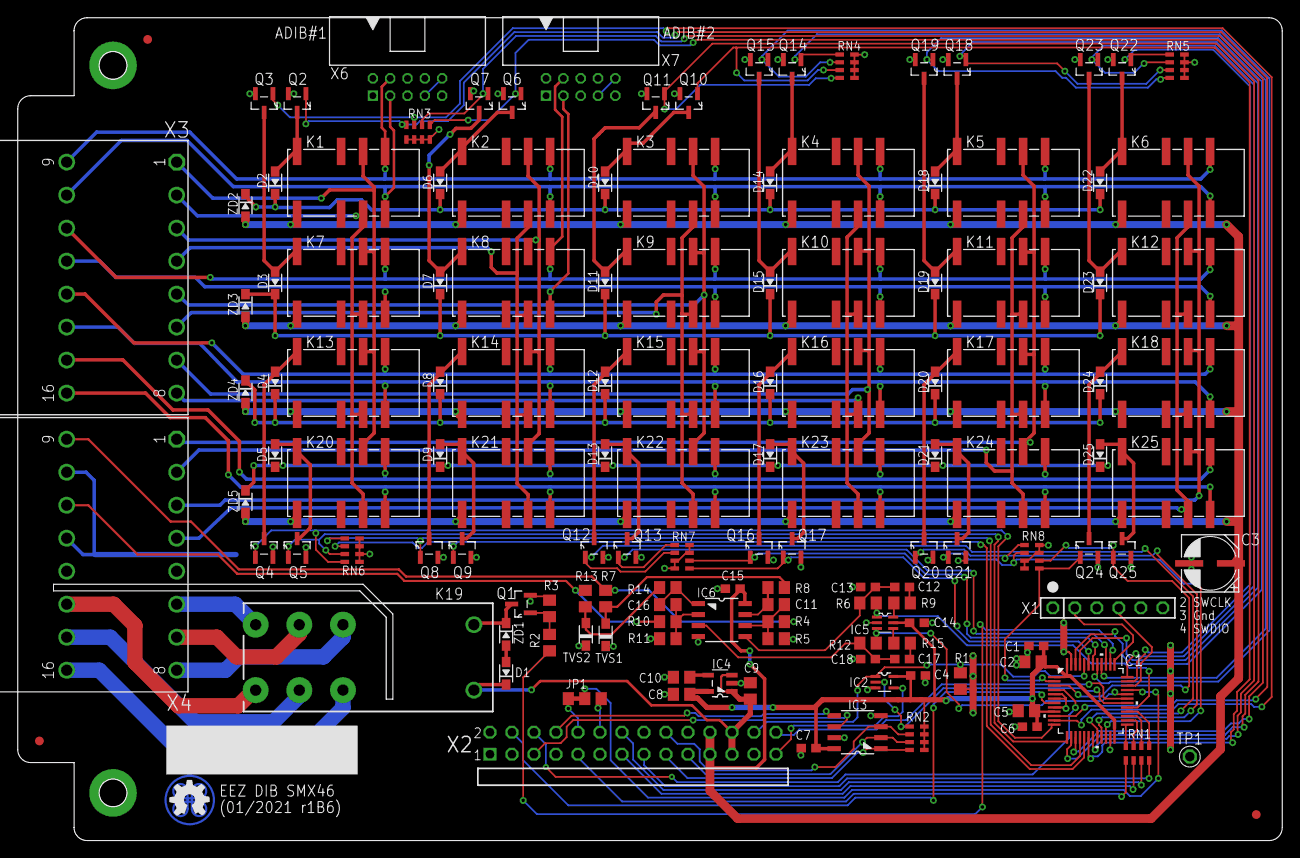
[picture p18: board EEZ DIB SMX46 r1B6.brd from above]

Board: 2 copper layers, 146.0 x 95.0 mm, 144 parts (1 on the bottom side), 129 nets.

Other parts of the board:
EEZ_SIGNATURE: SIGNATURESMALL; SIGNATURE_5MM

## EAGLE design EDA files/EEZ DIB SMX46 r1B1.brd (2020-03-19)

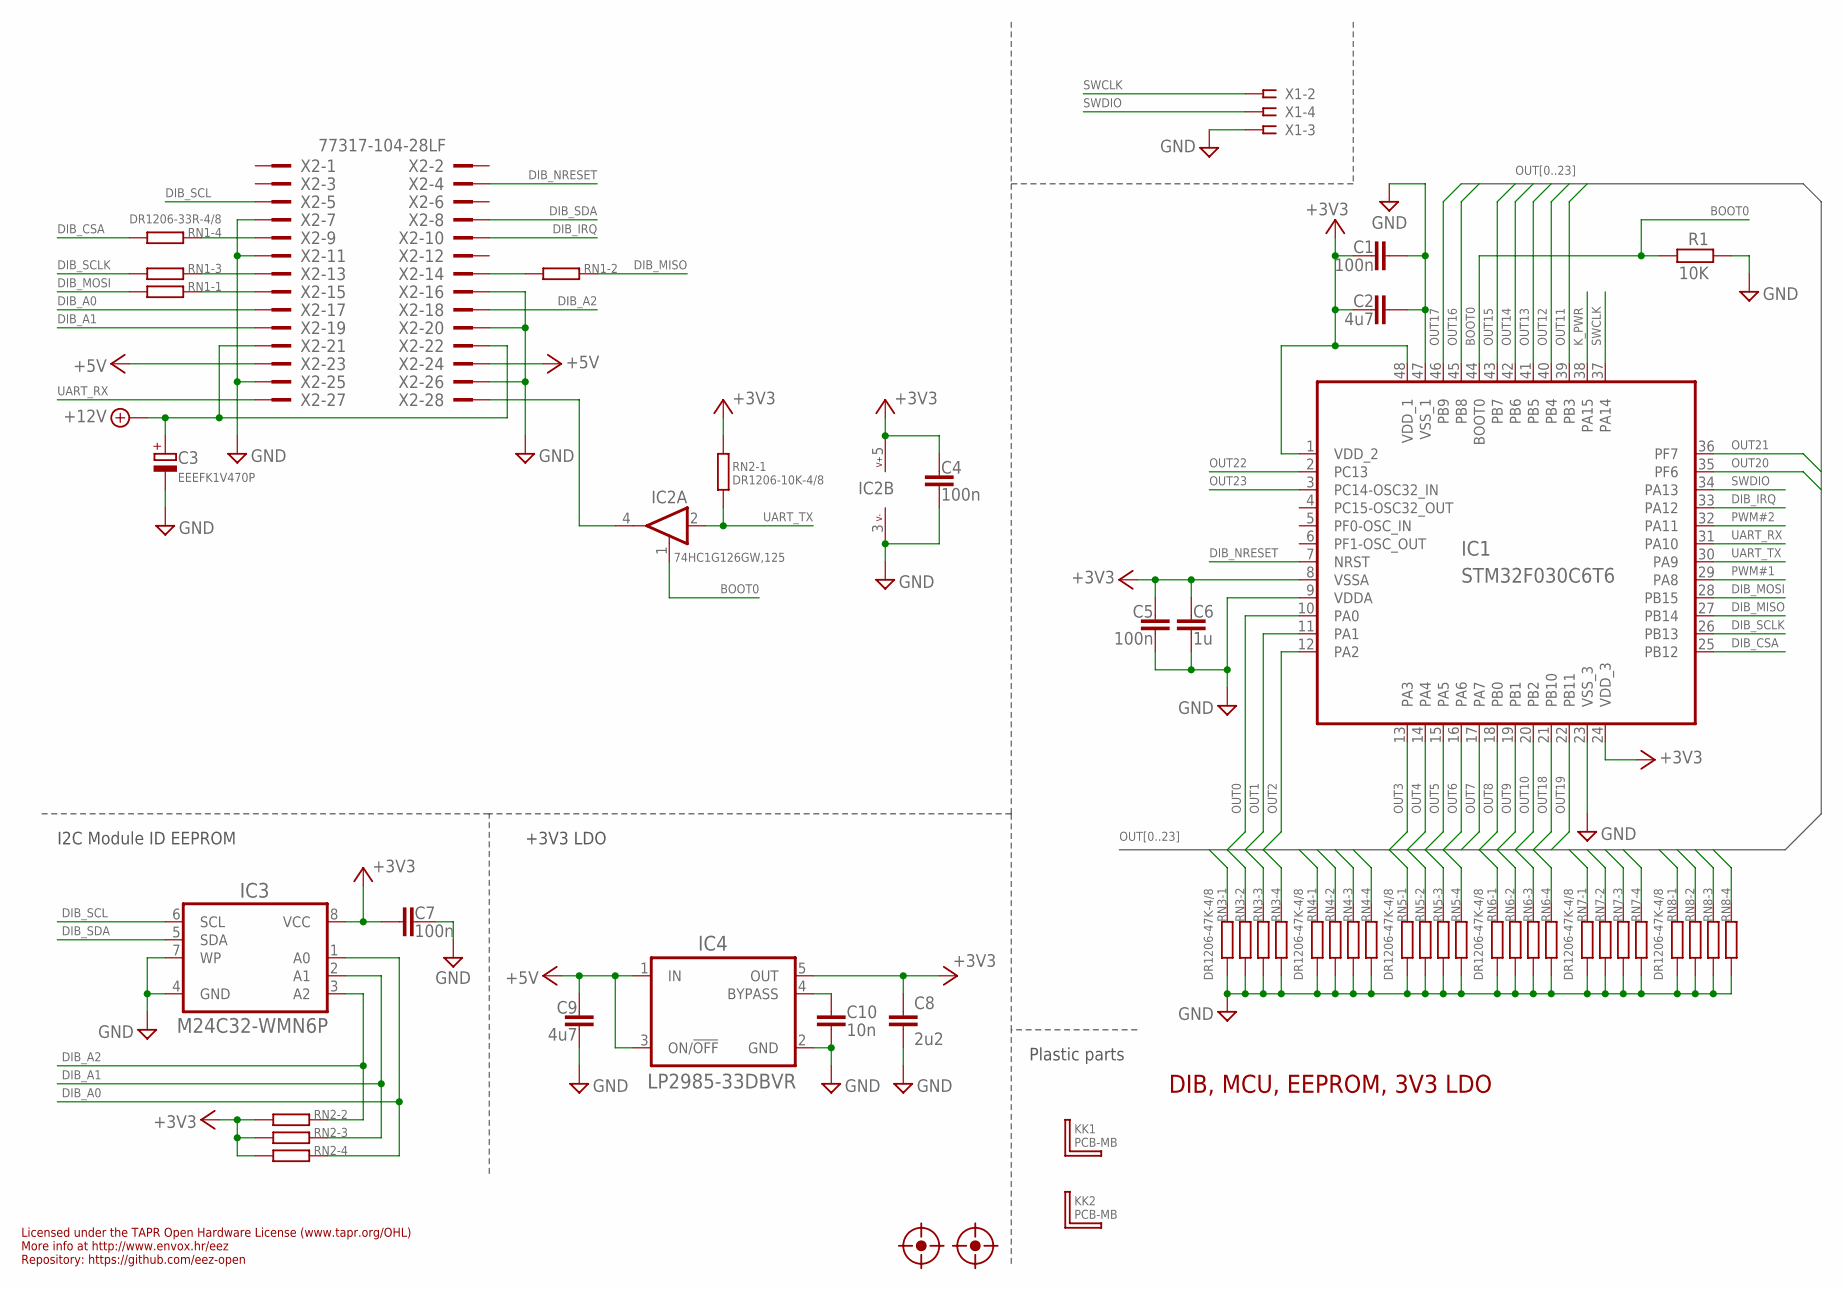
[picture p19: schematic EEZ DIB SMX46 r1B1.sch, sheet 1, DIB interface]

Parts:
C1, C4, C5, C7: 100n; C0603
C2, C9: 4u7; C1206
C3: EEEFK1V470P; CAPAE660X610N
C6: 1u; C0805
C8: 2u2; C0805
C10: 10n; C0805
FM1, FM2: FIDUCIAL_2; FIDUCIAL_DUAL
IC1: STM32F030C6T6; LQFP-48
IC2: 74HC1G126GW,125; SOT65P210X110-5N
IC3: M24C32-WMN6P; SOIC127P600X173-8N
IC4: LP2985-33DBVR; SOT95P270X145-5N
KK1, KK2: PCB-MB
R1: 10K; R0805
RN1: DR1206-33R-4/8; CAY16
RN2: DR1206-10K-4/8; CAY16
RN3, RN4, RN5, RN6, RN7, RN8: DR1206-47K-4/8; CAY16
X1: SSW-106-02-S-S
X2: 77317-104-28LF

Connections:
+3V3: C1.2, C2.1, C4.1, C5.1, C6.2, C7.2, C8.1, IC1.1 (VDD_2), IC1.8 (VSSA), IC1.24 (VDD_3), IC1.48 (VDD_1), IC2.5 (V+), IC3.8 (VCC), IC4.5 (OUT), RN2.5 (2), RN2.6 (2), RN2.7 (2), RN2.8 (2); also elsewhere on the board
+5V: C9.2, IC4.1 (IN), IC4.3 (ON/!OFF), X2.23, X2.24; also elsewhere on the board
+12V: C3.1 (+), X2.21, X2.22; also elsewhere on the board
BOOT0: IC1.44 (BOOT0), IC2.1 (EN), R1.2
DIB_A0: IC3.1 (A0), RN2.4 (1), X2.17
DIB_A1: IC3.2 (A1), RN2.3 (1), X2.19
DIB_A2: IC3.3 (A2), RN2.2 (1), X2.18
DIB_CSA: IC1.25 (PB12), RN1.4 (1)
DIB_IRQ: IC1.33 (PA12), X2.10
DIB_MISO: IC1.27 (PB14), RN1.2 (1)
DIB_MOSI: IC1.28 (PB15), RN1.1
DIB_NRESET: IC1.7 (NRST), X2.4
DIB_SCL: IC3.6 (SCL), X2.5
DIB_SCLK: IC1.26 (PB13), RN1.3 (1)
DIB_SDA: IC3.5 (SDA), X2.8
GND: C1.1, C2.2, C3.2 (-), C4.2, C5.2, C6.1, C7.1, C8.2, C9.1, C10.1, IC1.9 (VDDA), IC1.23 (VSS_3), IC1.47 (VSS_1), IC2.3 (V-), IC3.4 (GND), IC3.7 (WP), IC4.2 (GND), R1.1, RN3.1, RN3.2 (1), RN3.3 (1), RN3.4 (1), RN4.1, RN4.2 (1), RN4.3 (1), RN4.4 (1), RN5.1, RN5.2 (1), RN5.3 (1), RN5.4 (1), RN6.1, RN6.2 (1), RN6.3 (1), RN6.4 (1), RN7.3 (1), RN7.4 (1), RN7.7 (2), RN7.8 (2), RN8.3 (1), RN8.4 (1), RN8.7 (2), RN8.8 (2), X1.3, X2.7, X2.11, X2.16, X2.20, X2.25, X2.26; also elsewhere on the board
K_PWR: IC1.38 (PA15); also elsewhere on the board
unnamed: RN1.5 (2), X2.9
unnamed: C10.2, IC4.4 (BYPASS)
unnamed: IC2.4 (O), X2.28
unnamed: RN1.6 (2), X2.13
unnamed: RN1.7 (2), X2.14
unnamed: RN1.8 (2), X2.15
OUT0: IC1.10 (PA0), RN3.8 (2); also elsewhere on the board
OUT1: IC1.11 (PA1), RN3.7 (2); also elsewhere on the board
OUT2: IC1.12 (PA2), RN6.8 (2); also elsewhere on the board
OUT3: IC1.13 (PA3), RN6.7 (2); also elsewhere on the board
OUT4: IC1.14 (PA4), RN3.5 (2); also elsewhere on the board
OUT5: IC1.15 (PA5), RN3.6 (2); also elsewhere on the board
OUT6: IC1.16 (PA6), RN6.5 (2); also elsewhere on the board
OUT7: IC1.17 (PA7), RN6.6 (2); also elsewhere on the board
OUT8: IC1.18 (PB0), RN4.7 (2); also elsewhere on the board
OUT9: IC1.19 (PB1), RN4.8 (2); also elsewhere on the board
OUT10: IC1.20 (PB2), RN7.6 (2); also elsewhere on the board
OUT11: IC1.39 (PB3), RN7.5 (2); also elsewhere on the board
OUT12: IC1.40 (PB4), RN4.5 (2); also elsewhere on the board
OUT13: IC1.41 (PB5), RN4.6 (2); also elsewhere on the board
OUT14: IC1.42 (PB6), RN7.2 (1); also elsewhere on the board
OUT15: IC1.43 (PB7), RN7.1; also elsewhere on the board
OUT16: IC1.45 (PB8), RN5.7 (2); also elsewhere on the board
OUT17: IC1.46 (PB9), RN5.8 (2); also elsewhere on the board
OUT18: IC1.21 (PB10), RN8.5 (2); also elsewhere on the board
OUT19: IC1.22 (PB11), RN8.6 (2); also elsewhere on the board
OUT20: IC1.35 (PF6), RN5.5 (2); also elsewhere on the board
OUT21: IC1.36 (PF7), RN5.6 (2); also elsewhere on the board
OUT22: IC1.2 (PC13), RN8.1; also elsewhere on the board
OUT23: IC1.3 (PC14-OSC32_IN), RN8.2 (1); also elsewhere on the board
PWM#1: IC1.29 (PA8); also elsewhere on the board
PWM#2: IC1.32 (PA11); also elsewhere on the board
SWCLK: IC1.37 (PA14), X1.2
SWDIO: IC1.34 (PA13), X1.4
UART_RX: IC1.31 (PA10), X2.27
UART_TX: IC1.30 (PA9), IC2.2 (I), RN2.1

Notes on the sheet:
Licensed under the TAPR Open Hardware License (www.tapr.org/OHL)
Repository: https://github.com/eez-open
More info at http://www.envox.hr/eez
DIB, MCU, EEPROM, 3V3 LDO
Plastic parts
I2C Module ID EEPROM
+3V3 LDO

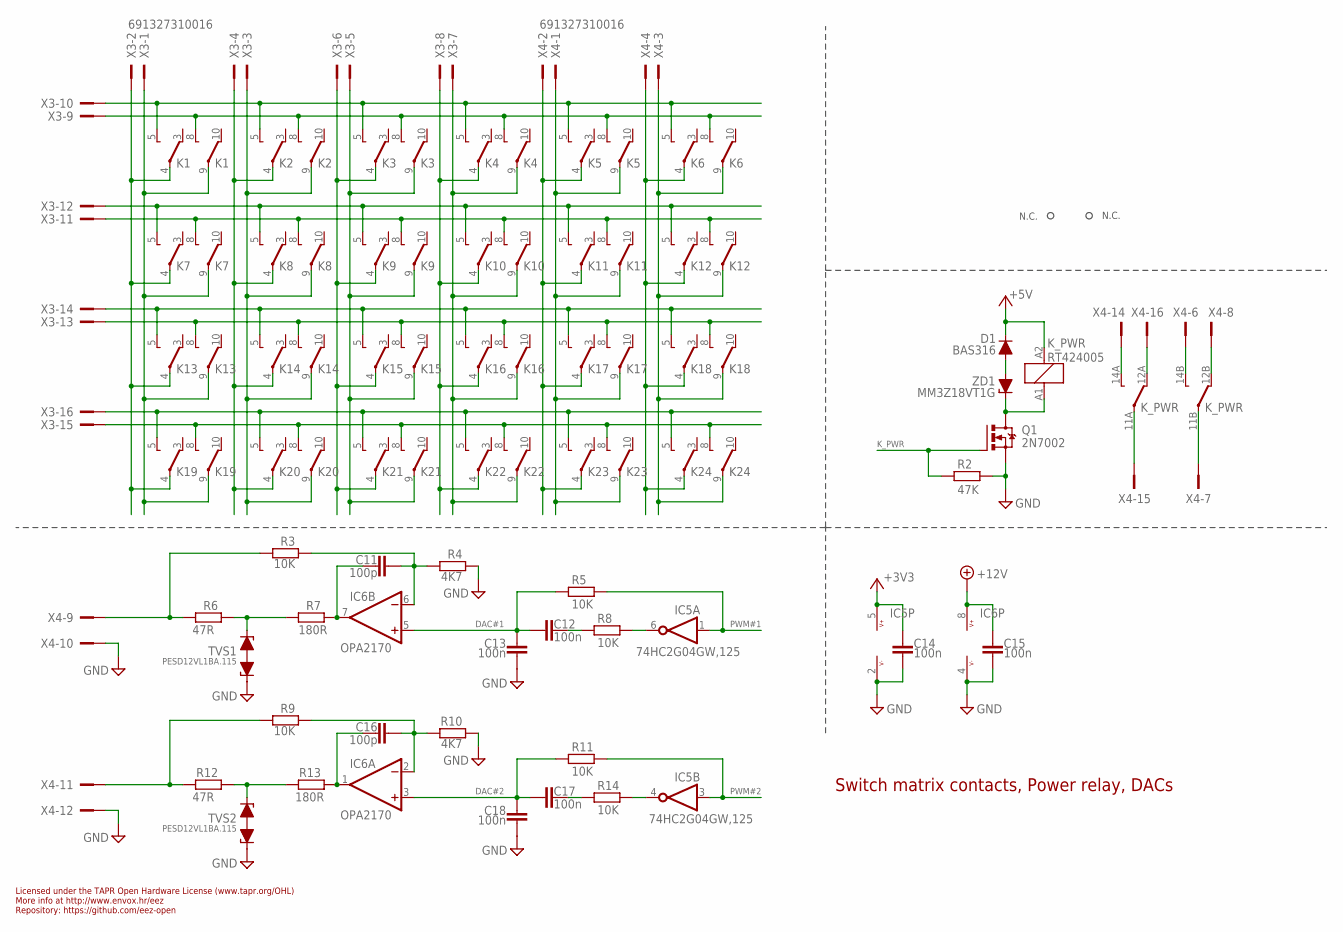
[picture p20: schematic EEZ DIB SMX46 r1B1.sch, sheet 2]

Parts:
C11, C16: 100p; C0805
C12, C13, C14, C15, C17, C18: 100n; C0603
D1: BAS316; SOD323-R
IC5: 74HC2G04GW,125; SOT65P210X110-6N
IC6: OPA2170; SOIC127P600X173-8N
K1, K2, K3, K4, K5, K6, K7, K8, K9, K10, K11, K12, K13, K14, K15, K16, K17, K18, K19, K20, K21, K22, K23, K24: FTR-C1GA012G-B05; FTR-C1
K_PWR: RT424005; RT-C/016A5_ROUND
Q1: 2N7002; SOT103P240X110-3N; MPN 2N7002-7-F
R2: 47K; R0805
R3, R5, R8, R9, R11, R14: 10K; R0805
R4, R10: 4K7; R0805
R6, R12: 47R; R0805
R7, R13: 180R; R0805
TVS1, TVS2: PESD12VL1BA.115; SOD323-BIDIR
X3, X4: 691327310016
ZD1: MM3Z18VT1G; SOD323-R

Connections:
+3V3: C14.1, IC5.5 (V+); also elsewhere on the board
+5V: D1.C, K_PWR.A2 (C1); also elsewhere on the board
+12V: C15.1, IC6.8 (V+); also elsewhere on the board
DAC#1: C12.1, C13.1, IC6.5 (+IN), R5.1
DAC#2: C17.1, C18.1, IC6.3 (+IN), R11.1
GND: C13.2, C14.2, C15.2, C18.2, IC5.2 (V-), IC6.4 (V-), Q1.2 (S), R2.1, R4.1, R10.1, TVS1.1, TVS2.1, X4.10, X4.12; also elsewhere on the board
ISET1: R6.1, R7.2, TVS1.2
ISET2: R12.1, R13.2, TVS2.2
K_PWR: Q1.1 (G), R2.2; also elsewhere on the board
unnamed: K1.4, K7.4, K13.4, K19.4, X3.2
unnamed: K1.9, K7.9, K13.9, K19.9, X3.1
unnamed: K13.5 (O), K14.5 (O), K15.5 (O), K16.5 (O), K17.5 (O), K18.5 (O), X3.14
unnamed: K13.8 (O), K14.8 (O), K15.8 (O), K16.8 (O), K17.8 (O), K18.8 (O), X3.13
unnamed: K7.5 (O), K8.5 (O), K9.5 (O), K10.5 (O), K11.5 (O), K12.5 (O), X3.12
unnamed: K7.8 (O), K8.8 (O), K9.8 (O), K10.8 (O), K11.8 (O), K12.8 (O), X3.11
unnamed: K19.5 (O), K20.5 (O), K21.5 (O), K22.5 (O), K23.5 (O), K24.5 (O), X3.16
unnamed: K19.8 (O), K20.8 (O), K21.8 (O), K22.8 (O), K23.8 (O), K24.8 (O), X3.15
unnamed: K5.4, K11.4, K17.4, K23.4, X4.2
unnamed: K2.4, K8.4, K14.4, K20.4, X3.4
unnamed: K2.9, K8.9, K14.9, K20.9, X3.3
unnamed: K5.9, K11.9, K17.9, K23.9, X4.1
unnamed: K6.4, K12.4, K18.4, K24.4, X4.4
unnamed: K6.9, K12.9, K18.9, K24.9, X4.3
unnamed: K3.4, K9.4, K15.4, K21.4, X3.6
unnamed: K3.9, K9.9, K15.9, K21.9, X3.5
unnamed: K4.4, K10.4, K16.4, K22.4, X3.8
unnamed: K4.9, K10.9, K16.9, K22.9, X3.7
unnamed: R3.2, R6.2, X4.9
unnamed: C17.2, R14.1
unnamed: IC5.4 (O), R14.2
unnamed: C11.1, IC6.7 (OUT), R7.1
unnamed: C16.2, IC6.2 (-IN), R9.1, R10.2
unnamed: C16.1, IC6.1 (OUT), R13.1
unnamed: K1.5 (O), K2.5 (O), K3.5 (O), K4.5 (O), K5.5 (O), K6.5 (O), X3.10
unnamed: K1.8 (O), K2.8 (O), K3.8 (O), K4.8 (O), K5.8 (O), K6.8 (O), X3.9
unnamed: K_PWR.11B, X4.7
unnamed: K_PWR.12B (S), X4.8
unnamed: R9.2, R12.2, X4.11
unnamed: K_PWR.14B (O), X4.6
unnamed: K_PWR.11A, X4.15
unnamed: K_PWR.12A (S), X4.16
unnamed: K_PWR.14A (O), X4.14
unnamed: D1.A, ZD1.A
unnamed: K_PWR.A1 (C2), Q1.3 (D), ZD1.C
unnamed: C12.2, R8.1
unnamed: C11.2, IC6.6 (-IN), R3.1, R4.2
unnamed: IC5.6 (O), R8.2
PWM#1: IC5.1 (I), R5.2; also elsewhere on the board
PWM#2: IC5.3 (I), R11.2; also elsewhere on the board

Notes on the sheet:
Licensed under the TAPR Open Hardware License (www.tapr.org/OHL)
Repository: https://github.com/eez-open
More info at http://www.envox.hr/eez
Switch matrix contacts, Power relay, DACs
N.C.

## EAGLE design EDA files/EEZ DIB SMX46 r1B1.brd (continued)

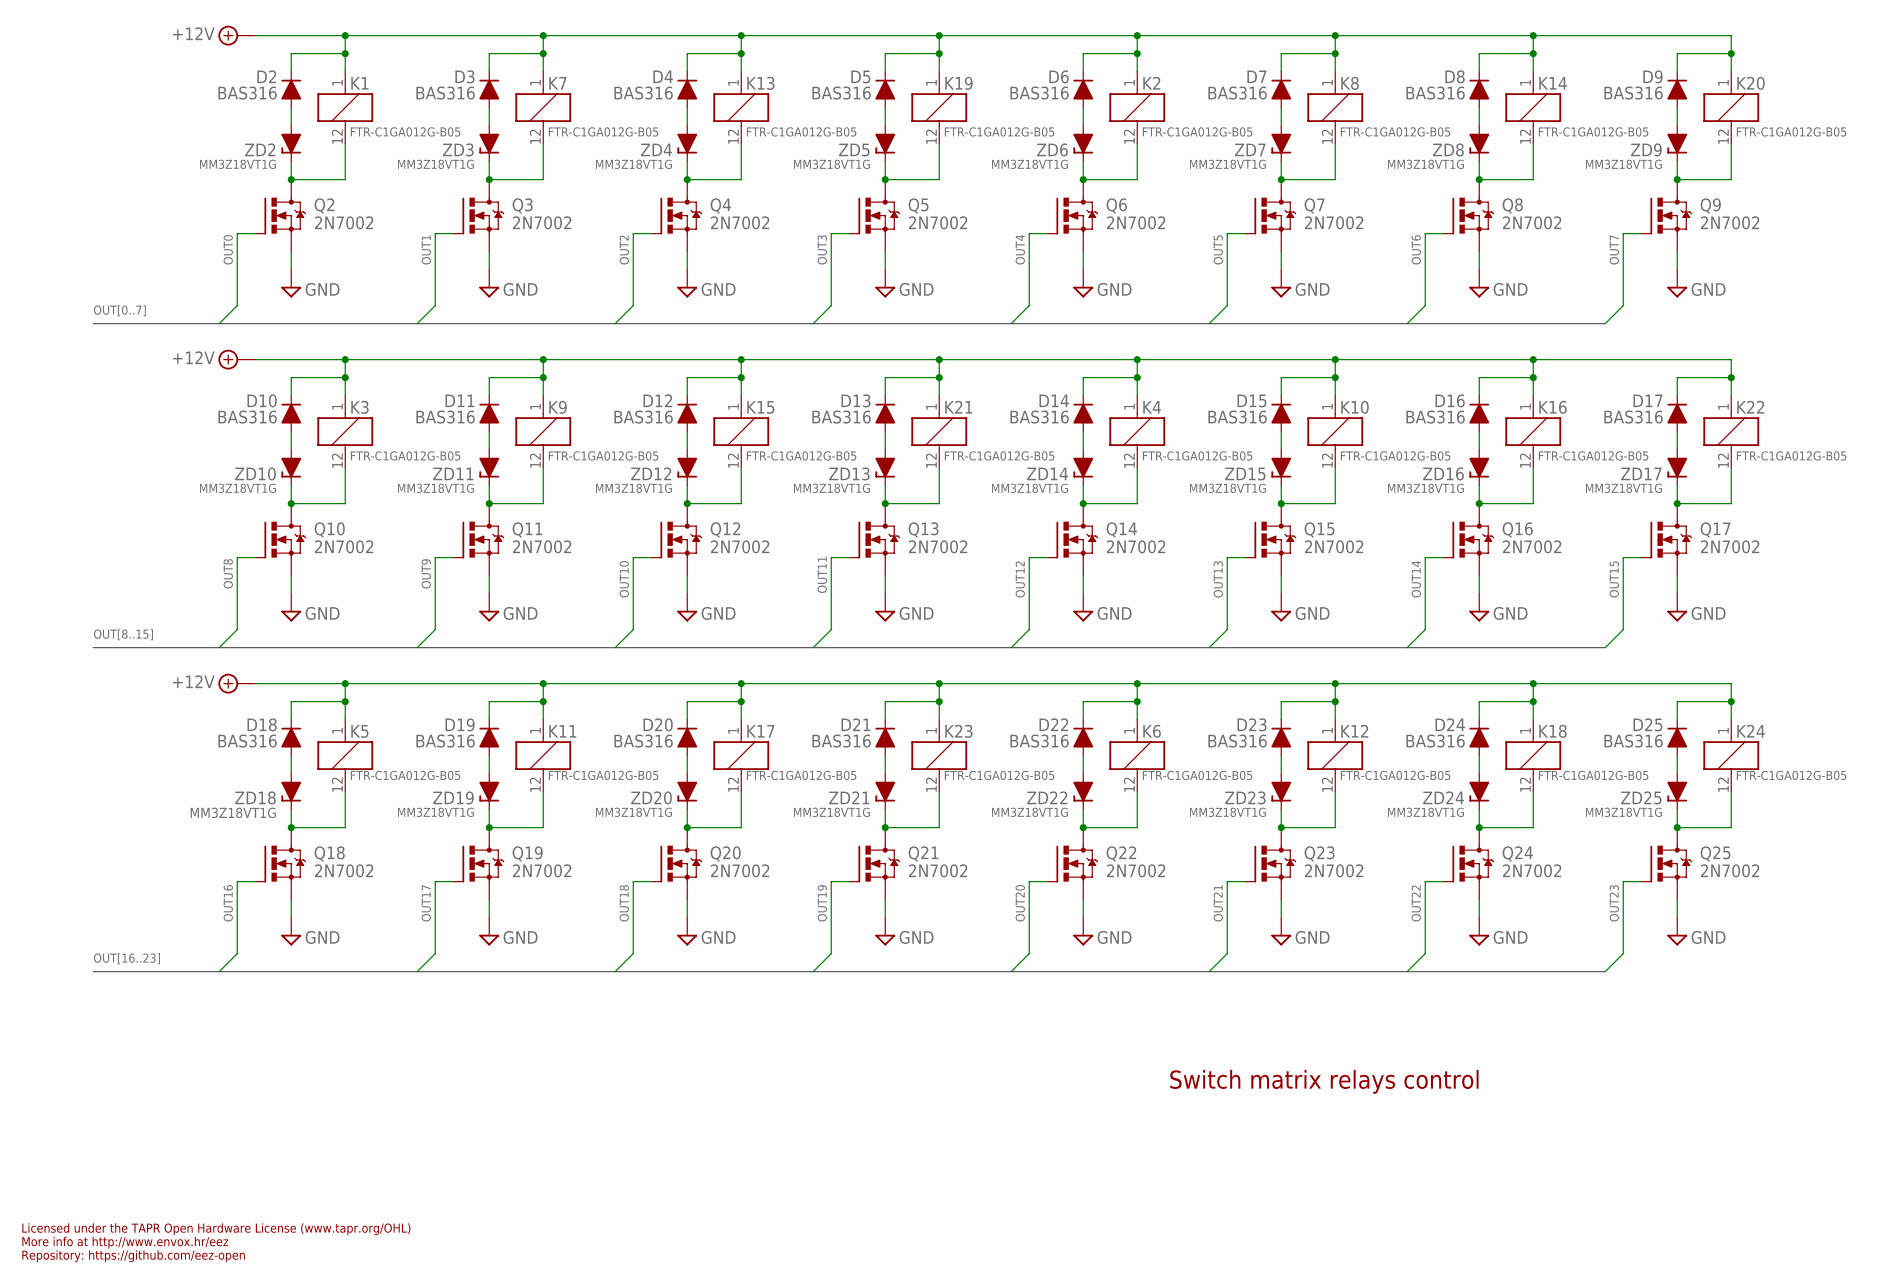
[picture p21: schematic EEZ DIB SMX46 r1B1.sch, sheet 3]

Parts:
D2, D3, D4, D5, D6, D7, D8, D9, D10, D11, D12, D13, D14, D15, D16, D17, D18, D19, D20, D21, D22, D23, D24, D25: BAS316; SOD323-R
K1, K2, K3, K4, K5, K6, K7, K8, K9, K10, K11, K12, K13, K14, K15, K16, K17, K18, K19, K20, K21, K22, K23, K24: FTR-C1GA012G-B05; FTR-C1
Q2, Q3, Q4, Q5, Q6, Q7, Q8, Q9, Q10, Q11, Q12, Q13, Q14, Q15, Q16, Q17, Q18, Q19, Q20, Q21, Q22, Q23, Q24, Q25: 2N7002; SOT103P240X110-3N; MPN 2N7002-7-F
ZD2, ZD3, ZD4, ZD5, ZD6, ZD7, ZD8, ZD9, ZD10, ZD11, ZD12, ZD13, ZD14, ZD15, ZD16, ZD17, ZD18, ZD19, ZD20, ZD21, ZD22, ZD23, ZD24, ZD25: MM3Z18VT1G; SOD323-R

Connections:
+12V: D2.C, D3.C, D4.C, D5.C, D6.C, D7.C, D8.C, D9.C, D10.C, D11.C, D12.C, D13.C, D14.C, D15.C, D16.C, D17.C, D18.C, D19.C, D20.C, D21.C, D22.C, D23.C, D24.C, D25.C, K1.1 (C1), K2.1 (C1), K3.1 (C1), K4.1 (C1), K5.1 (C1), K6.1 (C1), K7.1 (C1), K8.1 (C1), K9.1 (C1), K10.1 (C1), K11.1 (C1), K12.1 (C1), K13.1 (C1), K14.1 (C1), K15.1 (C1), K16.1 (C1), K17.1 (C1), K18.1 (C1), K19.1 (C1), K20.1 (C1), K21.1 (C1), K22.1 (C1), K23.1 (C1), K24.1 (C1); also elsewhere on the board
GND: Q2.2 (S), Q3.2 (S), Q4.2 (S), Q5.2 (S), Q6.2 (S), Q7.2 (S), Q8.2 (S), Q9.2 (S), Q10.2 (S), Q11.2 (S), Q12.2 (S), Q13.2 (S), Q14.2 (S), Q15.2 (S), Q16.2 (S), Q17.2 (S), Q18.2 (S), Q19.2 (S), Q20.2 (S), Q21.2 (S), Q22.2 (S), Q23.2 (S), Q24.2 (S), Q25.2 (S); also elsewhere on the board
unnamed: D4.A, ZD4.A
unnamed: K13.12 (C2), Q4.3 (D), ZD4.C
unnamed: D10.A, ZD10.A
unnamed: D8.A, ZD8.A
unnamed: K14.12 (C2), Q8.3 (D), ZD8.C
unnamed: K3.12 (C2), Q10.3 (D), ZD10.C
unnamed: D9.A, ZD9.A
unnamed: K20.12 (C2), Q9.3 (D), ZD9.C
unnamed: D11.A, ZD11.A
unnamed: K9.12 (C2), Q11.3 (D), ZD11.C
unnamed: D7.A, ZD7.A
unnamed: K8.12 (C2), Q7.3 (D), ZD7.C
unnamed: D12.A, ZD12.A
unnamed: K15.12 (C2), Q12.3 (D), ZD12.C
unnamed: D6.A, ZD6.A
unnamed: K2.12 (C2), Q6.3 (D), ZD6.C
unnamed: D13.A, ZD13.A
unnamed: K21.12 (C2), Q13.3 (D), ZD13.C
unnamed: D3.A, ZD3.A
unnamed: K7.12 (C2), Q3.3 (D), ZD3.C
unnamed: D14.A, ZD14.A
unnamed: K4.12 (C2), Q14.3 (D), ZD14.C
unnamed: D2.A, ZD2.A
unnamed: K1.12 (C2), Q2.3 (D), ZD2.C
unnamed: D15.A, ZD15.A
unnamed: K10.12 (C2), Q15.3 (D), ZD15.C
unnamed: D5.A, ZD5.A
unnamed: K19.12 (C2), Q5.3 (D), ZD5.C
unnamed: D16.A, ZD16.A
unnamed: K16.12 (C2), Q16.3 (D), ZD16.C
unnamed: D17.A, ZD17.A
unnamed: K22.12 (C2), Q17.3 (D), ZD17.C
unnamed: D19.A, ZD19.A
unnamed: K11.12 (C2), Q19.3 (D), ZD19.C
unnamed: D20.A, ZD20.A
unnamed: K17.12 (C2), Q20.3 (D), ZD20.C
unnamed: D21.A, ZD21.A
unnamed: K23.12 (C2), Q21.3 (D), ZD21.C
unnamed: D22.A, ZD22.A
unnamed: K6.12 (C2), Q22.3 (D), ZD22.C
unnamed: D23.A, ZD23.A
unnamed: K12.12 (C2), Q23.3 (D), ZD23.C
unnamed: D18.A, ZD18.A
unnamed: K5.12 (C2), Q18.3 (D), ZD18.C
unnamed: D24.A, ZD24.A
unnamed: K18.12 (C2), Q24.3 (D), ZD24.C
unnamed: D25.A, ZD25.A
unnamed: K24.12 (C2), Q25.3 (D), ZD25.C
OUT0: Q2.1 (G); also elsewhere on the board
OUT1: Q3.1 (G); also elsewhere on the board
OUT2: Q4.1 (G); also elsewhere on the board
OUT3: Q5.1 (G); also elsewhere on the board
OUT4: Q6.1 (G); also elsewhere on the board
OUT5: Q7.1 (G); also elsewhere on the board
OUT6: Q8.1 (G); also elsewhere on the board
OUT7: Q9.1 (G); also elsewhere on the board
OUT8: Q10.1 (G); also elsewhere on the board
OUT9: Q11.1 (G); also elsewhere on the board
OUT10: Q12.1 (G); also elsewhere on the board
OUT11: Q13.1 (G); also elsewhere on the board
OUT12: Q14.1 (G); also elsewhere on the board
OUT13: Q15.1 (G); also elsewhere on the board
OUT14: Q16.1 (G); also elsewhere on the board
OUT15: Q17.1 (G); also elsewhere on the board
OUT16: Q18.1 (G); also elsewhere on the board
OUT17: Q19.1 (G); also elsewhere on the board
OUT18: Q20.1 (G); also elsewhere on the board
OUT19: Q21.1 (G); also elsewhere on the board
OUT20: Q22.1 (G); also elsewhere on the board
OUT21: Q23.1 (G); also elsewhere on the board
OUT22: Q24.1 (G); also elsewhere on the board
OUT23: Q25.1 (G); also elsewhere on the board

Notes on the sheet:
Licensed under the TAPR Open Hardware License (www.tapr.org/OHL)
Repository: https://github.com/eez-open
More info at http://www.envox.hr/eez
Switch matrix relays control

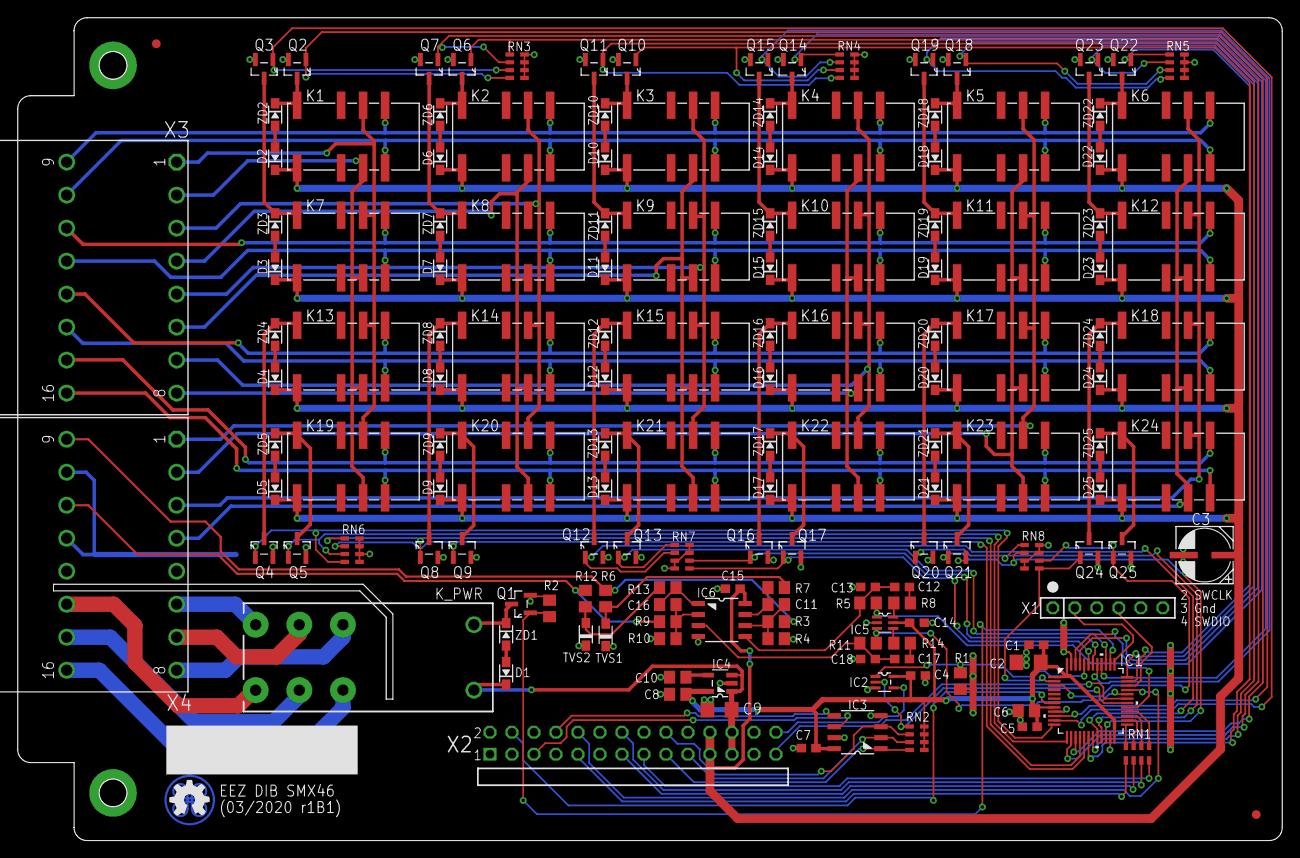
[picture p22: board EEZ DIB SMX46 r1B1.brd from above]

Board: 2 copper layers, 146.0 x 95.0 mm, 157 parts (0 on the bottom side), 143 nets.

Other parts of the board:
EEZ_SIGNATURE: SIGNATURESMALL; SIGNATURE_5MM

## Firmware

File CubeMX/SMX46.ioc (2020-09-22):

#MicroXplorer Configuration settings - do not modify
Dma.Request0=SPI1_RX
Dma.Request1=SPI1_TX
Dma.RequestsNb=2
Dma.SPI1_RX.0.Direction=DMA_PERIPH_TO_MEMORY
Dma.SPI1_RX.0.Instance=DMA1_Channel2
Dma.SPI1_RX.0.MemDataAlignment=DMA_MDATAALIGN_BYTE
Dma.SPI1_RX.0.MemInc=DMA_MINC_ENABLE
Dma.SPI1_RX.0.Mode=DMA_NORMAL
Dma.SPI1_RX.0.PeriphDataAlignment=DMA_PDATAALIGN_BYTE
Dma.SPI1_RX.0.PeriphInc=DMA_PINC_DISABLE
Dma.SPI1_RX.0.Priority=DMA_PRIORITY_LOW
Dma.SPI1_RX.0.RequestParameters=Instance,Direction,PeriphInc,MemInc,PeriphDataAlignment,MemDataAlignment,Mode,Priority
Dma.SPI1_TX.1.Direction=DMA_MEMORY_TO_PERIPH
Dma.SPI1_TX.1.Instance=DMA1_Channel3
Dma.SPI1_TX.1.MemDataAlignment=DMA_MDATAALIGN_BYTE
Dma.SPI1_TX.1.MemInc=DMA_MINC_ENABLE
Dma.SPI1_TX.1.Mode=DMA_NORMAL
Dma.SPI1_TX.1.PeriphDataAlignment=DMA_PDATAALIGN_BYTE
Dma.SPI1_TX.1.PeriphInc=DMA_PINC_DISABLE
Dma.SPI1_TX.1.Priority=DMA_PRIORITY_LOW
Dma.SPI1_TX.1.RequestParameters=Instance,Direction,PeriphInc,MemInc,PeriphDataAlignment,MemDataAlignment,Mode,Priority
File.Version=6
GPIO.groupedBy=Group By Peripherals
KeepUserPlacement=false
Mcu.Family=STM32F0
Mcu.IP0=CRC
Mcu.IP1=DMA
Mcu.IP2=NVIC
Mcu.IP3=RCC
Mcu.IP4=SPI1
Mcu.IP5=SYS
Mcu.IP6=TIM1
Mcu.IP7=USART1
Mcu.IPNb=8
Mcu.Name=STM32F030C6Tx
Mcu.Package=LQFP48
Mcu.Pin0=PC13
Mcu.Pin1=PC14-OSC32_IN
Mcu.Pin10=PA7
Mcu.Pin11=PB0
Mcu.Pin12=PB1
Mcu.Pin13=PB2
Mcu.Pin14=PB10
Mcu.Pin15=PB11
Mcu.Pin16=PB12
Mcu.Pin17=PB13
Mcu.Pin18=PB14
Mcu.Pin19=PB15
Mcu.Pin2=PC15-OSC32_OUT
Mcu.Pin20=PA8
Mcu.Pin21=PA9
Mcu.Pin22=PA10
Mcu.Pin23=PA11
Mcu.Pin24=PA12
Mcu.Pin25=PA13
Mcu.Pin26=PF6
Mcu.Pin27=PF7
Mcu.Pin28=PA14
Mcu.Pin29=PA15
Mcu.Pin3=PA0
Mcu.Pin30=PB3
Mcu.Pin31=PB4
Mcu.Pin32=PB5
Mcu.Pin33=PB6
Mcu.Pin34=PB7
Mcu.Pin35=PB8
Mcu.Pin36=PB9
Mcu.Pin37=VP_CRC_VS_CRC
Mcu.Pin38=VP_SYS_VS_Systick
Mcu.Pin4=PA1
Mcu.Pin5=PA2
Mcu.Pin6=PA3
Mcu.Pin7=PA4
Mcu.Pin8=PA5
Mcu.Pin9=PA6
Mcu.PinsNb=39
Mcu.ThirdPartyNb=0
Mcu.UserConstants=
Mcu.UserName=STM32F030C6Tx
MxCube.Version=5.6.1
MxDb.Version=DB.5.0.60
NVIC.DMA1_Channel2_3_IRQn=true\:0\:0\:false\:false\:true\:false\:true
NVIC.ForceEnableDMAVector=true
NVIC.HardFault_IRQn=true\:0\:0\:false\:false\:true\:false\:false
NVIC.NonMaskableInt_IRQn=true\:0\:0\:false\:false\:true\:false\:false
NVIC.PendSV_IRQn=true\:0\:0\:false\:false\:true\:false\:false
NVIC.SVC_IRQn=true\:0\:0\:false\:false\:true\:false\:false
NVIC.SysTick_IRQn=true\:0\:0\:false\:false\:true\:false\:true
PA0.GPIOParameters=GPIO_Label
PA0.GPIO_Label=OUT0
PA0.Locked=true
PA0.Signal=GPIO_Output
PA1.GPIOParameters=GPIO_Label
PA1.GPIO_Label=OUT1
PA1.Locked=true
PA1.Signal=GPIO_Output
PA10.Locked=true
PA10.Mode=Asynchronous
PA10.Signal=USART1_RX
PA11.GPIOParameters=GPIO_Label
PA11.GPIO_Label=PWM2
PA11.Signal=S_TIM1_CH4
PA12.GPIOParameters=GPIO_Label
PA12.GPIO_Label=DIB_IRQ
PA12.Locked=true
PA12.Signal=GPIO_Output
PA13.Mode=Serial_Wire
PA13.Signal=SYS_SWDIO
PA14.Mode=Serial_Wire
PA14.Signal=SYS_SWCLK
PA15.GPIOParameters=GPIO_Label
PA15.GPIO_Label=K_PWR
PA15.Locked=true
PA15.Signal=GPIO_Output
PA2.GPIOParameters=GPIO_Label
PA2.GPIO_Label=OUT2
PA2.Locked=true
PA2.Signal=GPIO_Output
PA3.GPIOParameters=GPIO_Label
PA3.GPIO_Label=OUT3
PA3.Locked=true
PA3.Signal=GPIO_Output
PA4.GPIOParameters=GPIO_Label
PA4.GPIO_Label=OUT4
PA4.Locked=true
PA4.Signal=GPIO_Output
PA5.GPIOParameters=GPIO_Label
PA5.GPIO_Label=OUT5
PA5.Locked=true
PA5.Signal=GPIO_Output
PA6.GPIOParameters=GPIO_Label
PA6.GPIO_Label=OUT6
PA6.Locked=true
PA6.Signal=GPIO_Output
PA7.GPIOParameters=GPIO_Label
PA7.GPIO_Label=OUT7
PA7.Locked=true
PA7.Signal=GPIO_Output
PA8.GPIOParameters=GPIO_Label
PA8.GPIO_Label=PWM1
PA8.Signal=S_TIM1_CH1
PA9.Locked=true
PA9.Mode=Asynchronous
PA9.Signal=USART1_TX
PB0.GPIOParameters=GPIO_Label
PB0.GPIO_Label=OUT8
PB0.Locked=true
PB0.Signal=GPIO_Output
PB1.GPIOParameters=GPIO_Label
PB1.GPIO_Label=OUT9
PB1.Locked=true
PB1.Signal=GPIO_Output
PB10.GPIOParameters=GPIO_Label
PB10.GPIO_Label=OUT18
PB10.Locked=true
PB10.Signal=GPIO_Output
PB11.GPIOParameters=GPIO_Label
PB11.GPIO_Label=OUT19
PB11.Locked=true
PB11.Signal=GPIO_Output
PB12.GPIOParameters=GPIO_Label
PB12.GPIO_Label=DIB_CSA
PB12.Mode=NSS_Signal_Hard_Input
PB12.Signal=SPI1_NSS
PB13.GPIOParameters=GPIO_Label
PB13.GPIO_Label=DIB_SCLK
PB13.Mode=Full_Duplex_Slave
PB13.Signal=SPI1_SCK
PB14.GPIOParameters=GPIO_Label
PB14.GPIO_Label=DIB_MISO
PB14.Mode=Full_Duplex_Slave
PB14.Signal=SPI1_MISO
PB15.GPIOParameters=GPIO_Label
PB15.GPIO_Label=DIB_MOSI
PB15.Mode=Full_Duplex_Slave
PB15.Signal=SPI1_MOSI
PB2.GPIOParameters=GPIO_Label
PB2.GPIO_Label=OUT10
PB2.Locked=true
PB2.Signal=GPIO_Output
PB3.GPIOParameters=GPIO_Label
PB3.GPIO_Label=OUT11
PB3.Locked=true
PB3.Signal=GPIO_Output
PB4.GPIOParameters=GPIO_Label
PB4.GPIO_Label=OUT12
PB4.Locked=true
PB4.Signal=GPIO_Output
PB5.GPIOParameters=GPIO_Label
PB5.GPIO_Label=OUT13
PB5.Locked=true
PB5.Signal=GPIO_Output
PB6.GPIOParameters=GPIO_Label
PB6.GPIO_Label=OUT14
PB6.Locked=true
PB6.Signal=GPIO_Output
PB7.GPIOParameters=GPIO_Label
PB7.GPIO_Label=OUT15
PB7.Locked=true
PB7.Signal=GPIO_Output
PB8.GPIOParameters=GPIO_Label
PB8.GPIO_Label=OUT16
PB8.Locked=true
PB8.Signal=GPIO_Output
PB9.GPIOParameters=GPIO_Label
PB9.GPIO_Label=OUT17
PB9.Locked=true
PB9.Signal=GPIO_Output
PC13.GPIOParameters=GPIO_Label
PC13.GPIO_Label=OUT22
PC13.Locked=true
PC13.Signal=GPIO_Output
PC14-OSC32_IN.GPIOParameters=GPIO_Label
PC14-OSC32_IN.GPIO_Label=OUT23
PC14-OSC32_IN.Locked=true
PC14-OSC32_IN.Signal=GPIO_Output
PC15-OSC32_OUT.GPIOParameters=GPIO_Label
PC15-OSC32_OUT.GPIO_Label=DIB_SYNC
PC15-OSC32_OUT.Locked=true
PC15-OSC32_OUT.Signal=GPIO_Input
PF6.GPIOParameters=GPIO_Label
PF6.GPIO_Label=OUT20
PF6.Locked=true
PF6.Signal=GPIO_Output
PF7.GPIOParameters=GPIO_Label
PF7.GPIO_Label=OUT21
PF7.Locked=true
PF7.Signal=GPIO_Output
PinOutPanel.RotationAngle=0
ProjectManager.AskForMigrate=true
ProjectManager.BackupPrevious=false
ProjectManager.CompilerOptimize=6
ProjectManager.ComputerToolchain=false
ProjectManager.CoupleFile=false
ProjectManager.CustomerFirmwarePackage=
ProjectManager.DefaultFWLocation=true
ProjectManager.DeletePrevious=true
ProjectManager.DeviceId=STM32F030C6Tx
ProjectManager.FirmwarePackage=STM32Cube FW_F0 V1.11.0
ProjectManager.FreePins=false
ProjectManager.HalAssertFull=false
ProjectManager.HeapSize=0x200
ProjectManager.KeepUserCode=true
ProjectManager.LastFirmware=false
ProjectManager.LibraryCopy=0
ProjectManager.MainLocation=Src
ProjectManager.NoMain=false
ProjectManager.PreviousToolchain=
ProjectManager.ProjectBuild=false
ProjectManager.ProjectFileName=SMX46.ioc
ProjectManager.ProjectName=SMX46
ProjectManager.StackSize=0x400
ProjectManager.TargetToolchain=EWARM V8.32
ProjectManager.ToolChainLocation=
ProjectManager.UnderRoot=false
ProjectManager.functionlistsort=
RCC.FamilyName=M
RCC.IPParameters=FamilyName,PLLCLKFreq_Value,PLLMCOFreq_Value,TimSysFreq_Value
RCC.PLLCLKFreq_Value=8000000
RCC.PLLMCOFreq_Value=8000000
RCC.TimSysFreq_Value=8000000
SH.S_TIM1_CH1.0=TIM1_CH1,Output Compare1 CH1
SH.S_TIM1_CH1.ConfNb=1
SH.S_TIM1_CH4.0=TIM1_CH4,PWM Generation4 CH4
SH.S_TIM1_CH4.ConfNb=1
SPI1.Direction=SPI_DIRECTION_2LINES
SPI1.IPParameters=VirtualType,Mode,Direction,VirtualNSS
SPI1.Mode=SPI_MODE_SLAVE
SPI1.VirtualNSS=VM_NSSHARD
SPI1.VirtualType=VM_SLAVE
TIM1.Channel-Output\ Compare1\ CH1=TIM_CHANNEL_1
TIM1.Channel-PWM\ Generation4\ CH4=TIM_CHANNEL_4
TIM1.IPParameters=Channel-PWM Generation4 CH4,Channel-Output Compare1 CH1
USART1.IPParameters=VirtualMode-Asynchronous
USART1.VirtualMode-Asynchronous=VM_ASYNC
VP_CRC_VS_CRC.Mode=CRC_Activate
VP_CRC_VS_CRC.Signal=CRC_VS_CRC
VP_SYS_VS_Systick.Mode=SysTick
VP_SYS_VS_Systick.Signal=SYS_VS_Systick
board=custom

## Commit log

2020-02-15 Eagle files added
    [EEZ DIB SMX46 r1B1.GBL, EEZ DIB SMX46 r1B1.GTL, EEZ DIB SMX46 r1B1.GTO, EEZ DIB SMX46 r1B1.GTS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]
2020-02-22 UART relocated
    [EEZ DIB SMX46 r1B1 raw.csv, EEZ DIB SMX46 r1B1.GBL, EEZ DIB SMX46 r1B1.GBO, EEZ DIB SMX46 r1B1.GTL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]
2020-02-26 debug connector update
    [EEZ DIB SMX46 r1B1.GBL, EEZ DIB SMX46 r1B1.GBS, EEZ DIB SMX46 r1B1.GTL, EEZ DIB SMX46 r1B1.GTO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]
2020-02-28 PCB terminals position adjusted
    [EEZ DIB SMX46 r1B1.GBL, EEZ DIB SMX46 r1B1.GBS, EEZ DIB SMX46 r1B1.GTL, EEZ DIB SMX46 r1B1.GTO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]
2020-02-29 IC2 package update
    [EEZ DIB SMX46 r1B1 raw.csv, EEZ DIB SMX46 r1B1.GBL, EEZ DIB SMX46 r1B1.GTL, EEZ DIB SMX46 r1B1.GTO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]
2020-03-19 front panel connectors position adjusted
    [EEZ DIB SMX46 r1B1.GBL, EEZ DIB SMX46 r1B1.GBS, EEZ DIB SMX46 r1B1.GTL, EEZ DIB SMX46 r1B1.GTO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]
2020-04-06 #1, #2 fixed
    [EEZ DIB SMX46 r1B2 BOM raw.csv, EEZ DIB SMX46 r1B2.GBL, EEZ DIB SMX46 r1B2.GBO, EEZ DIB SMX46 r1B2.GBS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]
2020-05-04 swap UART TX and RX
    [EEZ DIB SMX46 r1B2.GBL, EEZ DIB SMX46 r1B2.GBO, EEZ DIB SMX46 r1B2.GBS, EEZ DIB SMX46 r1B2.GTL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]
2020-05-18 prototype picture
2020-06-12 DIB alternative IRQs added
    [EEZ DIB SMX46 r1B2.GBL, EEZ DIB SMX46 r1B2.GBO, EEZ DIB SMX46 r1B2.GTL, EEZ DIB SMX46 r1B2.GTO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]
2020-09-19 BOM added
    [EEZ DIB SMX46 r1B2 BOM raw.csv, EEZ DIB SMX46 r1B2 BOM.ods, EEZ DIB SMX46 r1B2.brd, EEZ DIB SMX46 r1B2.sch]
2020-09-20 front panel labels update
    [EEZ DIB SMX46 r1B2.brd, EEZ DIB SMX46 r1B2.sch]
2020-09-20 Gerbers update
    [EEZ DIB SMX46 r1B2.GBL, EEZ DIB SMX46 r1B2.GTL, EEZ DIB SMX46 r1B2.GTO, EEZ DIB SMX46 r1B2.GTS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]
2020-09-20 C6 value
    [EEZ DIB SMX46 r1B2 BOM.ods, EEZ DIB SMX46 r1B2.GBL, EEZ DIB SMX46 r1B2.GTL, EEZ DIB SMX46 r1B2.brd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]
2020-10-25 prototype r1B2 picture
2020-12-02 #4, OSHW UID
    [EEZ DIB SMX46 r1B3.GBL, EEZ DIB SMX46 r1B3.GBO, EEZ DIB SMX46 r1B3.GBS, EEZ DIB SMX46 r1B3.GTL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]
2020-12-02 #5, BOM update
    [EEZ DIB SMX46 r1B2 BOM.ods, EEZ DIB SMX46 r1B4.GTL, EEZ DIB SMX46 r1B4.GTS, EEZ DIB SMX46 r1B5 BOM.ods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]
2020-12-13 ADIB ID=001
    [EEZ DIB SMX46 r1B5 BOM.ods, EEZ DIB SMX46 r1B6.GBL, EEZ DIB SMX46 r1B6.GBO, EEZ DIB SMX46 r1B6.GBS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]
2020-12-21 RN2 value update
    [EEZ DIB SMX46 r1B5 BOM.ods, EEZ DIB SMX46 r1B6 BOM.ods, EEZ DIB SMX46 r1B6.brd, EEZ DIB SMX46 r1B6.sch]
2021-01-16 r1B5 prototype picture
2021-01-30 PCB ID added
    [EEZ DIB SMX46 r1B6.GBO, EEZ DIB SMX46 r1B6.GTL, EEZ DIB SMX46 r1B6.GTO, EEZ DIB SMX46 r1B6.brd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]
2021-01-31 BOM update
    [EEZ DIB SMX46 r1B6 BOM.ods]
2021-03-25 BOM header date fix
    [EEZ DIB SMX46 r1B6 BOM.ods]
2021-03-25 Centroid files
    [EEZ DIB SMX46 r1B6.GBP, EEZ DIB SMX46 r1B6.GTP, EEZ DIB SMX46 r1B6_centroid.csv]

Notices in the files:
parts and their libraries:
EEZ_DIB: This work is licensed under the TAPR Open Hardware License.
